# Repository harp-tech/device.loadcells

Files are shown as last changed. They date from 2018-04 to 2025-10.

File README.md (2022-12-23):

## Harp Load Cells Interface and Reader

This pair of boards can be used to acquire analog signals from load cells and output their data to a USB host. It is additionally able to emit programmable digital events.

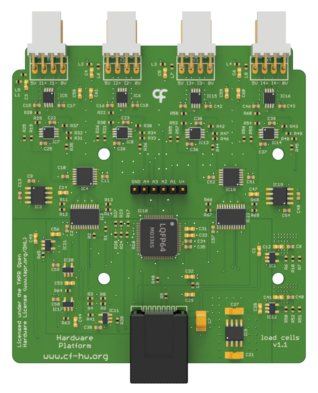
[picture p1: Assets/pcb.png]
harploadcellsinterface


### Key Features ###

* Load cells interface
  * Controls up to 2 load cells readers
  * Digital outputs can be regulated at 3V or 5V
* Load Cells Reader
  * Up to 4 load cell sensors
  * 1kHz sampling rate
  * Load cells offset compensation

### Connectivity ###

* Load cells interface
  * 1x BNC input signal (IN0)
  * 1x BNC output signal (Out0)
  * 1x screw terminal connector interface (GND, DOUT1 to DOUT8, DIN0)
  * 2x RJ45 for digital inputs (from load cells devices)
  * 1x stereo jack for clock sync input (CLKIN)
  * 1x USB (for computer)
  * 1x power barrel connector jack (12V only)
  * 1x screw terminal connector for 5V output (GND, +5V)
* Load Cells Reader
  * 4x flick lock connectors (X1 to X4) with 4 analog inputs each (5V, I+, I-, 0V)
  * 1x digital output [RJ45]

## Interface ##

The interface with the Harp board can be done through [Bonsai](https://bonsai-rx.org/) or a dedicated GUI (Graphical User Interface).

In order to use this GUI, there are some software that needs to be installed:

1 - Install the [drivers](https://bitbucket.org/fchampalimaud/downloads/downloads/UsbDriver-2.12.26.zip).

2 - Install the [runtime](https://bitbucket.org/fchampalimaud/downloads/downloads/Runtime-1.0.zip).

3 - Reboot the computer.

4 - Install the [GUI](https://bitbucket.org/fchampalimaud/downloads/downloads/Harp%20Load%20Cells%20v1.1.0.zip).

## Licensing ##

Each subdirectory will contain a license or, possibly, a set of licenses if it involves both hardware and software.

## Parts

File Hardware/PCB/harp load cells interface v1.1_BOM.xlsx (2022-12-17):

Part(s) | Quantity | Description | Distributor | Part. No.
IC1 | 1 | ESD Protection Low Cap | Mouser | 511-USBLC6-2SC6Y
IC2 | 1 | Conversores CC/CC sem isolação 12Vin, 0.591-6Vout 1.5A, Positive Logic | Mouser | 580-OKR-T/1.5-W12-C
IC3 | 1 | IC USB USB to Serial UART Enhanced IC SSOP-28 | Mouser | 895-FT232RL
IC4 | 1 | Reguladores de tensão de LDO High PSRR Fast RF High-Enable 1.5A | Mouser | 595-TPS78601DCQR
IC5 | 1 | Isoladores digitais Quad Ch 3.75V Iso 150M 2/2 NB, DO=LO | Mouser | 634-SI8642BC-B-IS1
IC6 | 1 | Microcontroladores de 8 bits - MCU 44TQFP, IND TEMP GREEN, 1.6-3.6V | Mouser | 556-ATXMEGA128A4U-AU
IC7 | 1 | LDO 250mA Ultra-Lo Noise LDO Reg | Mouser | 595-LP5907MFX-3.3NPB
IC8, IC9, IC10, IC11, IC12, IC13, IC14, IC15, IC16, IC17 | 10 | M74VHC1GT50DTT1G Buffer, Non-Inverting, 1.65V to 5.5V, SOT-23-5 | Mouser | 863-M74VHC1GT50DTT1G
C16 | 1 | CAP CER 13pF 50V ±5% C0G 0402 | Mouser | 81-GRM1555C1H130JA1D
C4, C5 | 2 | CAP CER 47pF 50V ±5% C0G 0402 | Mouser | 77-VJ0402A470JXACBC
CUSB | 1 | CAP CER 4.7nF 100V ±10% X7R 0402 | Mouser | 81-GRM155R72A472KA01
C2, C8, C10, C11, C15, C17, C19, C22, C23, C24, C25, C28, C29, C30, C31, C32, C33, C34, C35, C36, C37 | 21 | CAP CER 100nF 10V X5R 0402 | REEL | REEL
C26 | 1 | CAP CER 0.33uF 10V ±10% X5R 0402 | Mouser | GRM155R61A334KE15D
C9 | 1 | CAP TAN 4.7uF 6.3V ±10% 1206 | Mouser | 80-T491A475K006
C14, C18, C20, C21, C27 | 5 | CAP CER 10uF 10V ±10% X5R 0603 | Mouser | 81-GRM188R61A106KE9D
C1 | 1 | CAP TAN 22uF 20V ±10% 1210 | Mouser | 667-20TQC22MYFB
C3, C7 | 2 | CAP CER 22uF 25V ±10% X5R 1210 | Mouser | 81-GRM32ER61E226KE15
C12, C13 | 2 | CAP CER 47uF 10V ±10% X5R 1210 | Mouser | 81-GRM32ER61A476KE20
C6 | 1 | CAP ELE 100uF 25V ±20% | Mouser | 667-EEE-FK1E101P
R1 | 1 | RES SMD 0Ω OHM 5% 0402 | Mouser | 667-ERJ-2GE0R00X
R16, R17, R18, R19, R20, R21, R24, R25, R26, R27, R28, R29, R30, R31 | 14 | RES SMD 0402 33Ω, ± 1% | Mouser | 71-CRCW0402-33-E3
R15 | 1 | RES SMD 68Ω OHM 5% 0402 | Mouser | 71-CRCW0402-68-E3
RTRIM | 1 | RES SMD 243Ω OHM 1% 0402 | Mouser | 667-ERJ-2RKF2430X
R22 | 1 | RES SMD 330Ω OHM 1% 0402 | Mouser | 667-ERJ-PA2F3300X
R6 | 1 | RES SMD 30.9kΩ 1% 0402 | Mouser | 71-CRCW0402-30.9K-E3
R5 | 1 | RES SMD 95.3kΩ 1% 0402 | Mouser | 667-ERJ-2RKF9532X
R8, R10, R12, R14, R23 | 5 | RES SMD 100kΩ 1% 0402 | REEL | REEL
RUSB | 1 | RES SMD 1MΩ 1% 0402 | Mouser | 652-CR0402FX-1004GLF
F1 | 0 | 0603SFS100F/32-2 - Fuse, Surface Mount, 0603SFS Series, 1 A, 32 VDC, Slow Blow, 0603 | Mouser | 650-0603SFS100F/32-2
STATE | 1 | LED, Green, 1.6mm x 0.8mm, 566 nm, 2.1 V, 20 mA, 15 mcd | Mouser | 78-TLMP1100-GS08
OSC1 | 1 | 32MHz 10ppm | Mouser | 998-1001CI5032.0000T
CLKIN | 1 | SMT 3.5 STEREO REEL | Mouser | 502-35RASMT2BHNTRX
L2 | 1 | Indutores fixos LPS4012 Low Profile 1.5uH 2.2A 20% SMD | Mouser | 994-LPS4012-152MRB
L1 | 1 | 40ohms 100MHz 1.5A Monolithic 0805 SMD | Mouser | 875-MI0805K400R-10
PDI | 1 | 6P DR UNSHRD HRD | Mouser | 649-67996-206HLF
J1, J2 | 2 | Conectores modulares/Conectores de Ethernet 8/8 R/A MOD JACK | Mouser | 571-2158771
 | 2 | Ethernet Cable, Patch Lead, Cat5e, RJ45 Plug to RJ45 Plug, Beige, 500 mm | Farnell | 1526101
USB | 1 | UX60-MB-5S8 | Mouser | 798-UX60-MB-5S8
USB Cable | 1 | USB A - MINI-B 1M BLACK | Mouser | 538-88732-8602
 | 1 | Tubos de Luz LED CML LIGHTPIPE | Mouser | 606-7513D2-L
JACK | 1 | CC PCB 2.1MM | Mouser | 163-179PH-EX
WALL ADAPTER | 1 | AC/DC Power Supply, Class II, Fixed, 1 Output, 90 V, 264 V, 12 W, 12 V | Farnell | VEL12US120-EU-JA
J1 | 1 | C-Grid III 90120 Series, Through Hole, Header, 3 Contacts, 2.54 mm | Mouser | 538-90120-0763
Jumper | 1 | Jumper (Busbar), Shunt, PCB Connectors, 2, 2.54 mm | Farnell | 4218176
IN0, OUT0 | 2 | CONN BNC JACK R/A 50 OHM | Mouser | 571-5227161-1
 | 1 | 20.1550M/2-E - Pluggable Terminal Block, 3.5 mm, 2 Ways, 28 AWG, 16 AWG, 1.5 mm², Screw | Farnell | 2575215
 | 1 | 20.1550M/10-E - Pluggable Terminal Block, 3.5 mm, 10 Ways, 28 AWG, 16 AWG, 1.5 mm², Screw | Farnell | 2575213
X2 | 1 | 20.155MH/2-E - Terminal Block, Header, 3.5 mm, 2 Ways, 10 A, 250 V, Through Hole Right Angle | Farnell | 2517858
X1 | 1 | 20.155MH/10-E - Terminal Block, Header, 3.5 mm, 10 Ways, 10 A, 250 V, Through Hole Right Angle | Farnell | 2575221
 | 8 | 1110030 - Nut, Hex, M3, Nylon 6.6, Pack of 50 | Farnell | 1110030
 | 4 | Machine Screw, M3, 10 mm, Nylon (Polyamide), Pan Head Slotted, PK25 | Farnell | 1514410
Components | 116
Licensed under the TAPR Open Hardware License (www.tapr.org/OHL)
Copyright 2018 Artur Silva and Filipe Carvalho

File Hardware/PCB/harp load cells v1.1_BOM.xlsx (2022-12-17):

Part(s) | Quantity | Description | Distributor | Part. No.
IC1 | 1 | Reguladores de tensão de LDO 20V 200mA LDO adjVo | Mouser | 584-ADP7118AUJZ-R7
IC2, IC22 | 2 | CIs de potenciômetros digitais IC 4-CH | Mouser | 584-AD5204BRUZ10-R7
IC3, IC19 | 2 | Referências de tensão Ultra-High-Precision Ultra-Low-Noise 3V | Mouser | 700-MAX6126AASA30
IC4, IC18 | 2 | Amplificadores de precisão 55V Low Noise Zero Drift OpAmp 4x | Mouser | 584-ADA4522-4ARUZ
IC4, IC18 | 0 | Amplificadores operacionais - 2.2nV/rtHz,18MHz Prec,RRO,36V | Mouser | 595-OPA4209AIPW
IC10 | 1 | ADC 4Ch w/Bipolar 16B Simult Sampling | Mouser | 584-AD7606BSTZ-4
IC9 | 1 | Reguladores de tensão de comutação 125mA Swtc Cap Volt Converter | Mouser | 700-MAX1680ESA
IC7, IC8, IC13, IC14 | 4 | Amplificadores operacionais - Amp Op 36V,microPwr,RRO Dual | Mouser | 595-OPA2170AIDGKR
IC11 | 1 | SINGLE BUS BUFFER GATE | Mouser | 595-SN74LVC1G125DBVR
IC12 | 1 | Reguladores de tensão de LDO -30V 200mA lo-noise Linear Reg adj | Mouser | 584-ADP7182AUJZ-R7
IC5, IC6, IC15, IC16 | 4 | Amplificadores de instrumentação 3nV/Hz Low Power | Mouser | 584-AD8421ARMZ-R7
IC5, IC6, IC15, IC16 | 0 | Amplificadores de instrumentação 330 uA Rail to Rail | Mouser | 584-AD8422-ARMZ
IC21 | 1 | LDO 200mA Low IQ LDO Reg for Portables | Mouser | 595-TLV70030DDCR
IC17 | 1 | Inversores 3-5.5V Single TTL Schmitt Input | Mouser | 863-M74VHC1GT14DTT1G
IC20 | 1 | Buffers e line drivers Single Schmitt-Trgr | Mouser | 595-SN74LVC1G17DBVG4
C2, C9, C10, C11, C13, C15, C16, C17, C18, C19, C20, C22, C23, C24, C25, C26, C30, C36, C37, C38, C39, C40, C42, C43, C45, C46, C48, C50, C51, C52, C54, C55, C57 | 33 | SMD 0402 100nF 16V X7R ±5% | REEL | REEL
C8, C34, C35 | 3 | SMD 0402 1uF 10V X7S ±10% | Mouser | 81-GCM155C71A105ME8D
C14, C47, C53 | 3 | SMD 0603 1uF 6.3V X6S ±10% | Mouser | 81-GRM185C80J105KE26
C1, C12, C28, C41, C58, C59, C60, C61 | 8 | SMD 0402 2.2uF 25V X5R ±20% | Mouser | 81-GRM188R61E225ME4D
C49, C56 | 2 | SMD 0603 4.7uF 10V X5R ±20% | Mouser | 81-GRM185R61A475ME1D
C3, C4, C5, C6, C29, C31, C32, C33, C44 | 9 | SMD 0603 10uF 16V ±20% | Mouser | 81-GRM188R61C106MALD
C21, C27 | 2 | SMD 10uF 25V ±10% B Case Molded | Mouser | 74-293D106X9025B2TE3
C7 | 1 | CAP TAN 22uF 20V ±10% 1210 | Mouser | 667-20TQC22MYFB
R5 | 1 | SMD 0402 0Ohms ±5% | Mouser | 667-ERJ-2GE0R00X
R2, R39, R40, R41 | 4 | SMD 0402 33Ohms ±5% | Mouser | 667-ERJ-2GEJ330X
R15, R16, R61, R62 | 4 | SMD 0402 100Ohms ±0.1% | Mouser | 667-ERA-2AEB101X
R15, R16, R61, R62 | 0 | SMD 0402 200Ohms ±0.1% | Mouser | 667-ERA-2ARB201X
R19, R20, R21, R22, R25, R26, R29, R30, R31, R32, R33, R34, R46, R47, R48, R49, R53, R54, R55, R56, R57, R58, R59, R60 | 24 | SMD 0402 1kOhms ±0.1% | Mouser | 667-ERA-2AEB102X
R1, R3, R8 | 3 | SMD 0402 3kOhms ±5% | Mouser | 667-ERJ-2GEJ302X
R11, R12, R13, R14, R66, R67, R68, R69 | 8 | SMD 0402 5.1kOhms ±5% | Mouser | 667-ERJ-2RKF5101X
R7, R10, R51, R52 | 4 | SMD 0402 10kOhm | REEL | REEL
R63 | 1 | SMD 0402 20kOhms ±5% | Mouser | 667-ERJ-2GEJ203X
R50 | 1 | SMD 0402 29.4kOhms ±1% | Mouser | 667-ERJ-2RKF2942X
R6 | 1 | SMD 0402 30kOhms ±1% | Mouser | 667-ERJ-2RKF3002X
R64 | 1 | SMD 0402 40.2kOhms ±1% | Mouser | 667-ERJ-2RKF4022X
R18, R23, R27, R65 | 4 | SMD 0402 100kOhm | REEL | REEL
R35, R36, R37, R38, R42, R43, R44, R45 | 8 | SMD 0402 12kOhms ±1% | Mouser | 667-ERJ-U02F1202X | 100g
R35, R36, R37, R38, R42, R43, R44, R45 | 0 | SMD 0402 36kOhms ±1% | Mouser | 652-CR0402FX-3602GLF | 33.3g
L1, L2, L3, L4, L5, L6, L7, L8, L9 | 9 | Indutores fixos 1uH 20% | Mouser | 810-MLZ1005M1R0WT000
J1 | 1 | Conectores modulares/Conectores de Ethernet 8/8 R/A MOD JACK | Mouser | 571-2158771
JP1 | 1 | HEADER 6x1 2.54mm GOLD | Mouser | 68001-206HLF
X1, X2, X3, X4 | 4 | Distribuidores e Alojamento de Fios 4C RA F/L HEADER | Mouser | 538-22-05-7048
 | 4 | Receptacle, 4 Ways, 2.54 mm, 2759, 4809 Series Crimp Terminals | Mouser | 538-22-01-2045
 | 16 | CRIMP TERM 22-30 TIN | Mouser | 538-08-50-0114
 | 8 | 1110030 - Nut, Hex, M3, Nylon 6.6, Pack of 50 | Farnell | 1110030
 | 4 | Machine Screw, M3, 10 mm, Nylon (Polyamide), Pan Head Slotted, PK25 | Farnell | 1514410
Components | 194
Licensed under the TAPR Open Hardware License (www.tapr.org/OHL)
Copyright 2018 Artur Silva and Filipe Carvalho

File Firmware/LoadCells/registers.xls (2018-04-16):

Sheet: registers
Has event. | When | Type | Array | Array Len. | Register Name | Desciption | Mask Type | Value | Name | Desciption
no |  | U8 | no |  | START | Writing any value above ZERO will start the acquisition. ZERO will stop it. | bit | (1<<0) | START
yes | When a new sample is acquired | I16 | yes | 8 | LOAD_CELLS | Analog value of the Load Cells
yes | When DI0_CONF == DI0_SYNC and the input changes | U8 | no |  | DI0 | State of digital input 0 (DI0) | bit | (1<<0) | DI0
yes | When DO0_CONF == DO0_TGL_EACH_SEC | U8 | no |  | DO0 | State of digital output 0 (DO0) | bit | (1<<0) | DO0
no |  | U8 | no |  | THRESHOLDS | State of the filter thresholds -- This regiter is not used!!!
no |  | U8 | no |  | RESERVED0 | Reserved for future purposes
no |  | U8 | no |  | RESERVED1 | Reserved for future purposes
no |  | U8 | no |  | DI0_CONF | Configuration of the digital input 0 (DI0) | mask | (3<<0) | DI0_SEL
 |  |  |  |  |  |  | group_mask | (0<<0) | DI0_SYNC | Use as a pure digital input
 |  |  |  |  |  |  | group_mask | (1<<0) | DI0_RISE_START_ACQ | Start acquisition when rising edge and stop when falling edge
 |  |  |  |  |  |  | group_mask | (2<<0) | DI0_FALL_START_ACQ | Start acquisition when falling edge and stop when rising edge
no |  | U8 | no |  | DO0_CONF | Configuration of the digital output 0 (DO0) | mask | (3<<0) | DO0_SEL
 |  |  |  |  |  |  | group_mask | (0<<0) | DO0_DIG | Use as a pure digital output
 |  |  |  |  |  |  | group_mask | (1<<0) | DO0_TGL_EACH_SEC | Toogle each second when acquiring
 |  |  |  |  |  |  | group_mask | (2<<0) | DO0_PULSE | The digital output will be ONE during period specified by register DO0_PULSE
no |  | U8 | no |  | DO0_PULSE | Pulse for the digital output 0 (DO0) [1:255]
no |  | U16 | no |  | DO_SET | Set the digital outputs
no |  | U16 | no |  | DO_CLEAR | Clear the digital outputs
no |  | U16 | no |  | DO_TOGGLE | Toggle the digital outputs
yes | When the values where changed by a threshold filter | U16 | no |  | DO_OUT | Writes to the digital output
no |  | U8 | no |  | RESERVED2 | Reserved for future purposes
no |  | U8 | no |  | RESERVED3 | Reserved for future purposes
no |  | I16 | no |  | OFFSET_CH0 | Offset value of Load Cell channel 0 [-255:255]
no |  | I16 | no |  | OFFSET_CH1 | Offset value of Load Cell channel 1 [-255:255]
no |  | I16 | no |  | OFFSET_CH2 | Offset value of Load Cell channel 2 [-255:255]
no |  | I16 | no |  | OFFSET_CH3 | Offset value of Load Cell channel 3 [-255:255]
no |  | I16 | no |  | OFFSET_CH4 | Offset value of Load Cell channel 4 [-255:255]
no |  | I16 | no |  | OFFSET_CH5 | Offset value of Load Cell channel 5 [-255:255]
no |  | I16 | no |  | OFFSET_CH6 | Offset value of Load Cell channel 6 [-255:255]
no |  | I16 | no |  | OFFSET_CH7 | Offset value of Load Cell channel 7 [-255:255]
no |  | U8 | no |  | RESERVED4 | Reserved for future purposes
no |  | U8 | no |  | RESERVED5 | Reserved for future purposes
 |  | U8 | no |  | DO0_CH | Load Cell channel to be used to feed the threshold filter | mask | (16<<0) | DO_CH
 |  | U8 | no |  | DO1_CH |  | group_mask | (0<<0) | CH0 | Load Cell channel 0
 |  | U8 | no |  | DO2_CH |  | group_mask | (1<<0) | CH1 | Load Cell channel 1
 |  | U8 | no |  | DO3_CH |  | group_mask | (2<<0) | CH2 | Load Cell channel 2
 |  | U8 | no |  | DO4_CH |  | group_mask | (3<<0) | CH3 | Load Cell channel 3
 |  | U8 | no |  | DO5_CH |  | group_mask | (4<<0) | CH4 | Load Cell channel 4
 |  | U8 | no |  | DO6_CH |  | group_mask | (5<<0) | CH5 | Load Cell channel 5
 |  | U8 | no |  | DO7_CH |  | group_mask | (6<<0) | CH6 | Load Cell channel 6
 |  | I16 | no |  | DO0_TH_VALUE | Value to be compared | group_mask | (7<<0) | CH7 | Load Cell channel 7
 |  | I16 | no |  | DO1_TH_VALUE |  | group_mask | (8<<0) | SOFTWARE | Filter not used -- Use pin as a pure digital output
 |  | I16 | no |  | DO2_TH_VALUE
 |  | I16 | no |  | DO3_TH_VALUE
 |  | I16 | no |  | DO4_TH_VALUE
 |  | I16 | no |  | DO5_TH_VALUE
 |  | I16 | no |  | DO6_TH_VALUE
 |  | I16 | no |  | DO7_TH_VALUE
 |  | U16 | no |  | DO0_TH_UP_MS | Time (ms) above the configured threshold to set the digital output
 |  | U16 | no |  | DO1_TH_UP_MS
 |  | U16 | no |  | DO2_TH_UP_MS
 |  | U16 | no |  | DO3_TH_UP_MS
 |  | U16 | no |  | DO4_TH_UP_MS
 |  | U16 | no |  | DO5_TH_UP_MS
 |  | U16 | no |  | DO6_TH_UP_MS
 |  | U16 | no |  | DO7_TH_UP_MS
 |  | U16 | no |  | DO0_TH_DOWN_MS | Time (ms) below the configured threshold to set the digital output
 |  | U16 | no |  | DO1_TH_DOWN_MS
 |  | U16 | no |  | DO2_TH_DOWN_MS
 |  | U16 | no |  | DO3_TH_DOWN_MS
 |  | U16 | no |  | DO4_TH_DOWN_MS
 |  | U16 | no |  | DO5_TH_DOWN_MS
 |  | U16 | no |  | DO6_TH_DOWN_MS
 |  | U16 | no |  | DO7_TH_DOWN_MS
no |  | U8 | no |  | EVNT_ENABLE | Enable the Events | bit | (1<<0) | EVT_LOAD_CELLS | Event of register LOAD_CELLS
 |  |  |  |  |  |  | bit | (1<<1) | EVT_DI0 | Event of register DI0
 |  |  |  |  |  |  | bit | (1<<2) | EVT_DO0 | Event of register DO0
 |  |  |  |  |  |  | bit | (1<<3) | EVT_DO_OUT | Event of THRESHOLDS

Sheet: meta data
who am I: | 1232
firmware major version: | 1
firmware minor version: | 0
hardware major version: | 1
hardware minor version: | 0
assembly version: | 0
device name: | LoadCells

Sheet: ios
Pin Name | PORT | Pin | Direction | Use Input | Out | Out default | Pull | Sense | Int. priority | Int. number | Desciption | Neg. Output
DI0 | PORTB | 0 | input |  |  |  | up | both_edges | low | 0 | Input DIO
DO0 | PORTB | 1 | output | yes | digital | 0 |  |  |  |  | Output DO0 | no
DO1 | PORTA | 0 | output | yes | digital | 0 |  |  |  |  | Output DO1 | no
DO2 | PORTA | 1 | output | yes | digital | 0 |  |  |  |  | Output DO2 | no
DO3 | PORTA | 2 | output | yes | digital | 0 |  |  |  |  | Output DO3 | no
DO4 | PORTA | 3 | output | yes | digital | 0 |  |  |  |  | Output DO4 | no
DO5 | PORTA | 4 | output | yes | digital | 0 |  |  |  |  | Output DO5 | no
DO6 | PORTA | 5 | output | yes | digital | 0 |  |  |  |  | Output DO6 | no
DO7 | PORTA | 6 | output | yes | digital | 0 |  |  |  |  | Output DO7 | no
DO8 | PORTA | 7 | output | yes | digital | 0 |  |  |  |  | Output DO8 | no
CS0_2 | PORTC | 1 | output | yes | wire_and | 1 |  |  |  |  | CS0_2 / CS_POT0 | no
CS0_1 | PORTC | 0 | output | yes | wire_and | 1 |  |  |  |  | CS0_1 / CS_ADC0 | no
CS0_0 | PORTC | 4 | output | yes | digital | 1 |  |  |  |  | CS0_0 / CONVST0 | no
MOSI0 | PORTC | 5 | output | no | digital | 0 |  |  |  |  | MOSI0 | no
MISO0 | PORTC | 6 | input |  |  |  | up | both_edges | off | 0 | MISO0
SCK0 | PORTC | 7 | output | no | digital | 0 |  |  |  |  | SCK0 | no
CS1_2 | PORTD | 1 | output | yes | wire_and | 1 |  |  |  |  | CS1_2 / CS_POT1 | no
CS1_1 | PORTD | 0 | output | yes | wire_and | 1 |  |  |  |  | CS1_1 / CS_ADC1 | no
CS1_0 | PORTD | 4 | output | yes | digital | 1 |  |  |  |  | CS1_0 / CONVST1 | no
MOSI1 | PORTD | 5 | output | no | digital | 0 |  |  |  |  | MOSI1 | no
MISO1 | PORTD | 6 | input |  |  |  | up | both_edges | off | 0 | MISO1
SCK1 | PORTD | 7 | output | no | digital | 0 |  |  |  |  | SCK1 | no

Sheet: options
Array | Type | Array | Bits type | Direction | Use input | Pull | Sense | Int. priority | Int. number | Int. Mask | Out | Neg. Output
 |  |  |  | input | yes | up | both_edges | low | 0 |  | digital | yes
yes | U8 | yes | bit | output | no | down | rising_edge | med | 1 |  | wire_or | no
no | U16 | no | mask |  |  | tristate | falling_edge | high |  |  | wire_and
 | U32 |  | group_mask |  |  | busholder | low_level | off |  |  | wired_or_pull
 | U64 |  |  |  |  |  | no_interrupt |  |  |  | wired_and_pull
 | I8
 | I16
 | I32
 | I64
 | FLOAT

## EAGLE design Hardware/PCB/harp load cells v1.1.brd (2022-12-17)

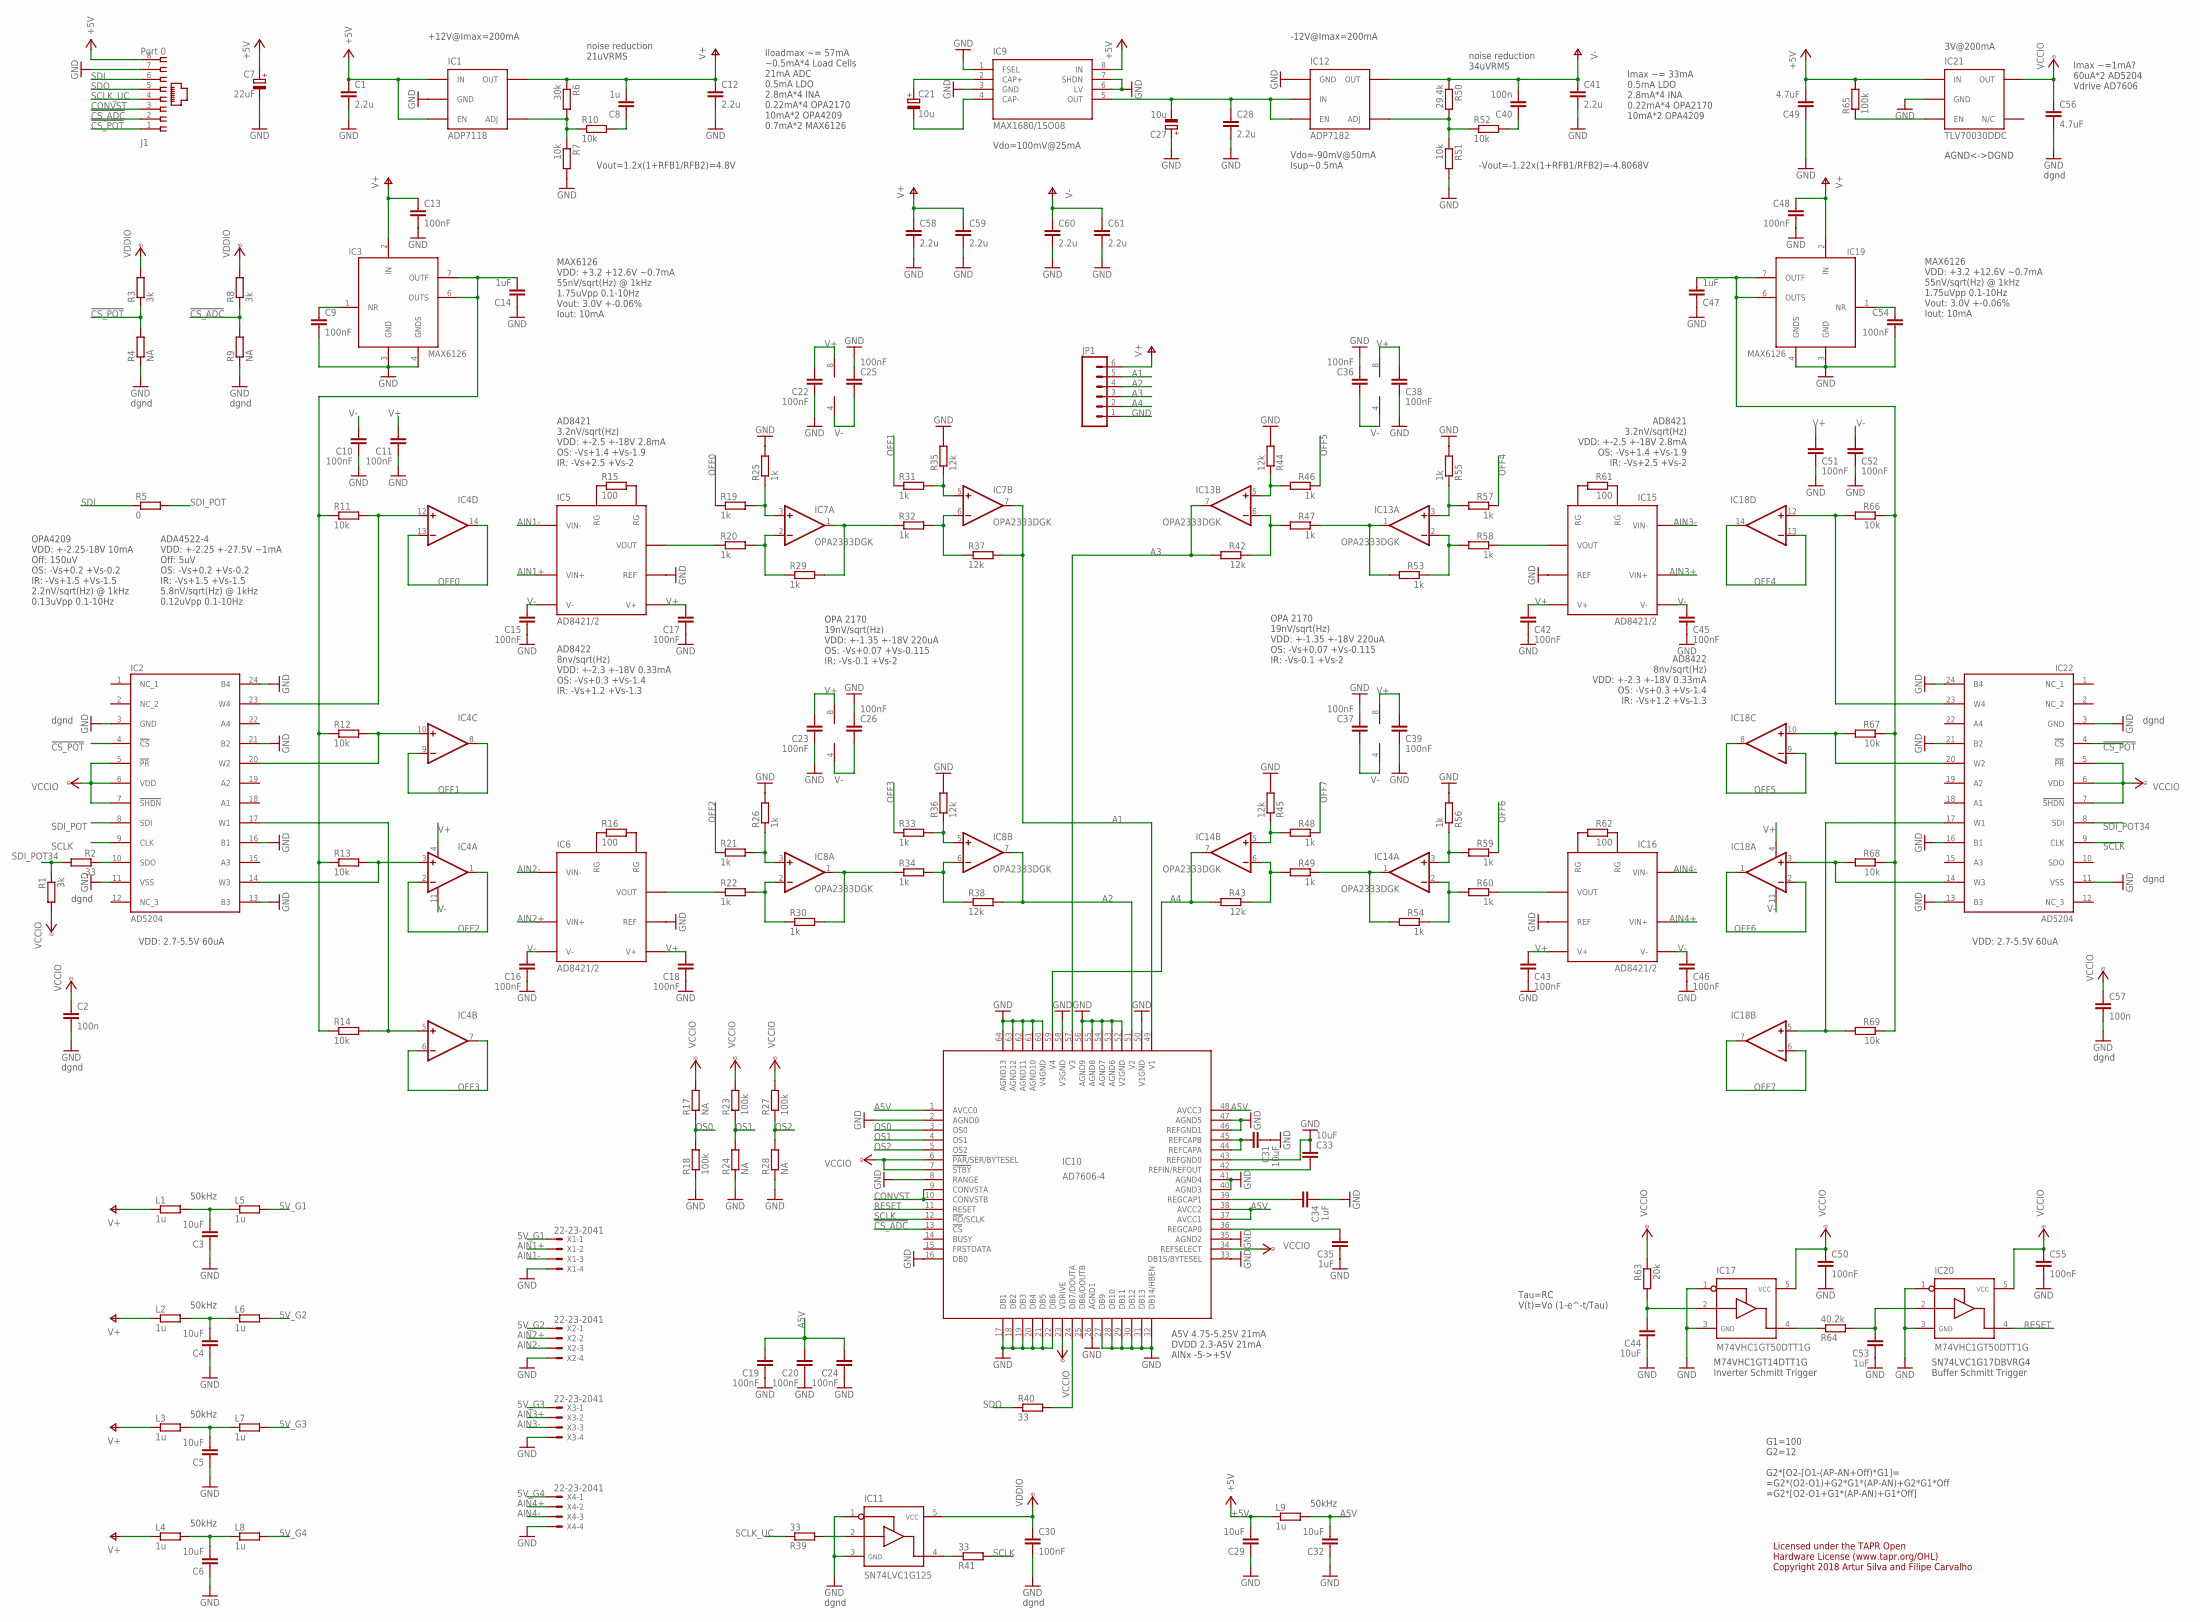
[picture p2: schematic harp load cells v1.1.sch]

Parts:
C1, C12, C28, C41, C58, C59, C60, C61: 2.2u; C0603
C2, C40, C57: 100n; C0402
C3, C4, C5, C6, C29, C31, C32, C33, C44: 10uF; C0603
C7: 22uF; CAP_100UF_HAND
C8: 1u; C0402
C9, C10, C11, C13, C15, C16, C17, C18, C19, C20, C22, C23, C24, C25, C26, C30, C36, C37, C38, C39, C42, C43, C45, C46, C48, C50, C51, C52, C54, C55: 100nF; C0402
C14, C47, C53: 1uF; C0603
C21, C27: 10u; A/3216-18W
C34, C35: 1uF; C0402
C49, C56: 4.7uF; C0603
IC1: ADP7118; TSOT23-5
IC2, IC22: AD5204; TSSOP-24
IC3, IC19: MAX6126; SO08
IC4, IC18: OPA4336T; TSSOP-14
IC5, IC6, IC15, IC16: AD8421/2; MSOP8
IC7, IC8, IC13, IC14: OPA2333DGK; MSOP08
IC9: MAX1680/1SO08; SO08
IC10: AD7606-4; LQFP-64
IC11: SN74LVC1G125; SOT23-5
IC12: ADP7182; TSOT23-5
IC17, IC20: M74VHC1GT50DTT1G; SOT23-5
IC21: TLV70030DDC; TSOT23-5
J1: Port 0; 520426-4
JP1: M06NO_SILK; 1X06_NO_SILK
L1, L2, L3, L4, L5, L6, L7, L8, L9: 1u; R0402
R1, R3, R8: 3k; R0402
R2, R39, R40, R41: 33; R0402
R4, R9, R17, R24, R28: NA; R0402
R5: 0; R0402
R6: 30k; R0402
R7, R10, R11, R12, R13, R14, R51, R52, R66, R67, R68, R69: 10k; R0402
R15, R16, R61, R62: 100; R0402
R18, R23, R27, R65: 100k; R0402
R19, R20, R21, R22, R25, R26, R29, R30, R31, R32, R33, R34, R46, R47, R48, R49, R53, R54, R55, R56, R57, R58, R59, R60: 1k; R0402
R35, R36, R37, R38, R42, R43, R44, R45: 12k; R0402
R50: 29.4k; R0402
R63: 20k; R0402
R64: 40.2k; R0402
X1, X2, X3, X4: 22-23-2041

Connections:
5V_G1: L5.2, X1.1
5V_G2: L6.2, X2.1
5V_G3: L7.2, X3.1
5V_G4: L8.2, X4.1
!CS_ADC: IC10.13 (!CS), J1.2, R8.1, R9.2
!CS_POT: IC2.4 (!CS), IC22.4 (!CS), J1.1, R3.1, R4.2
+5V: C1.1, C7.+, C29.2, C49.2, IC1.1 (IN), IC1.3 (EN), IC9.8 (IN), IC21.1 (IN), J1.8, L9.1, R65.2
A1: IC7.7 (OUT), IC10.49 (V1), JP1.5, R37.2
A2: IC8.7 (OUT), IC10.51 (V2), JP1.4, R38.2
A3: IC10.57 (V3), IC13.7 (OUT), JP1.3, R42.2
A4: IC10.59 (V4), IC14.7 (OUT), JP1.2, R43.2
A5V: C19.2, C20.2, C24.2, C32.2, IC10.1 (AVCC0), IC10.37 (AVCC1), IC10.38 (AVCC2), IC10.48 (AVCC3), L9.2
AIN1+: IC5.P$4 (VIN+), X1.2
AIN1-: IC5.P$1 (VIN-), X1.3
AIN2+: IC6.P$4 (VIN+), X2.2
AIN2-: IC6.P$1 (VIN-), X2.3
AIN3+: IC15.P$4 (VIN+), X3.2
AIN3-: IC15.P$1 (VIN-), X3.3
AIN4+: IC16.P$4 (VIN+), X4.2
AIN4-: IC16.P$1 (VIN-), X4.3
CONVST: IC10.9 (CONVSTA), IC10.10 (CONVSTB), J1.3
GND: C1.2, C2.2, C3.1, C4.1, C5.1, C6.1, C7.-, C9.2, C10.1, C11.1, C12.2, C13.2, C14.1, C15.1, C16.1, C17.1, C18.1, C19.1, C20.1, C22.1, C23.1, C24.1, C25.1, C26.1, C27.+, C28.2, C29.1, C30.2, C31.1, C32.1, C33.1, C34.1, C35.1, C36.1, C37.1, C38.1, C39.1, C41.2, C42.1, C43.1, C44.1, C45.1, C46.1, C47.1, C48.2, C49.1, C50.2, C51.1, C52.1, C53.1, C54.2, C55.2, C56.2, C57.2, C58.2, C59.2, C60.2, C61.2, IC1.2 (GND), IC2.3 (GND), IC2.11 (VSS), IC2.13 (B3), IC2.16 (B1), IC2.21 (B2), IC2.24 (B4), IC3.3 (GND), IC3.4 (GNDS), IC5.P$6 (REF), IC6.P$6 (REF), IC9.1 (FSEL), IC9.3 (GND), IC9.6 (LV), IC9.7 (SHDN), IC10.2 (AGND0), IC10.8 (RANGE), IC10.16 (DB0), IC10.17 (DB1), IC10.18 (DB2), IC10.19 (DB3), IC10.20 (DB4), IC10.21 (DB5), IC10.22 (DB6), IC10.26 (AGND1), IC10.27 (DB9), IC10.28 (DB10), IC10.29 (DB11), IC10.30 (DB12), IC10.31 (DB13), IC10.32 (DB14/HBEN), IC10.33 (DB15/BYTESEL), IC10.35 (AGND2), IC10.40 (AGND3), IC10.41 (AGND4), IC10.43 (REFGND0), IC10.46 (REFGND1), IC10.47 (AGND5), IC10.50 (V1GND), IC10.52 (V2GND), IC10.53 (AGND6), IC10.54 (AGND7), IC10.55 (AGND8), IC10.56 (AGND9), IC10.58 (V3GND), IC10.60 (V4GND), IC10.61 (AGND10), IC10.62 (AGND11), IC10.63 (AGND12), IC10.64 (AGND13), IC11.1, IC11.3, IC12.1 (GND), IC15.P$6 (REF), IC16.P$6 (REF), IC17.1, IC17.3, IC19.3 (GND), IC19.4 (GNDS), IC20.1, IC20.3, IC21.2 (GND), IC22.3 (GND), IC22.11 (VSS), IC22.13 (B3), IC22.16 (B1), IC22.21 (B2), IC22.24 (B4), J1.7, JP1.1, R4.1, R7.2, R9.1, R18.1, R24.1, R25.2, R26.2, R28.1, R35.2, R36.2, R44.2, R45.2, R51.2, R55.2, R56.2, X1.4, X2.4, X3.4, X4.4
unnamed: IC21.3 (EN), R65.1
unnamed: IC12.4 (ADJ), R50.2, R51.1, R52.1
unnamed: C44.2, IC17.2, R63.2
unnamed: C35.2, IC10.36 (REGCAP0)
unnamed: IC6.P$7 (VOUT), R22.1
unnamed: C40.1, R52.2
unnamed: C6.2, L4.2, L8.1
unnamed: IC17.4, R64.1
unnamed: C21.+, IC9.2 (CAP+)
unnamed: C21.-, IC9.4 (CAP-)
unnamed: C27.-, C28.1, IC9.5 (OUT), IC12.2 (IN), IC12.3 (EN)
unnamed: C53.2, IC20.2, R64.2
unnamed: IC7.6 (-IN), R32.2, R37.1
unnamed: C34.2, IC10.39 (REGCAP1)
unnamed: IC13.2 (-IN), R53.1, R58.2
unnamed: IC7.2 (-IN), R20.2, R29.1
unnamed: IC7.3 (+IN), R19.2, R25.1
unnamed: IC7.5 (+IN), R31.2, R35.1
unnamed: C33.2, IC10.42 (REFIN/REFOUT)
unnamed: IC13.3 (+IN), R55.1, R57.2
unnamed: IC13.6 (-IN), R42.1, R47.2
unnamed: IC13.5 (+IN), R44.1, R46.2
unnamed: C31.2, IC10.44 (REFCAPA), IC10.45 (REFCAPB)
unnamed: C8.1, R10.2
unnamed: IC1.4 (ADJ), R6.2, R7.1, R10.1
unnamed: IC5.P$2 (RG), R15.2
unnamed: IC5.P$3 (RG), R15.1
unnamed: IC5.P$7 (VOUT), R20.1
unnamed: IC8.2 (-IN), R22.2, R30.1
unnamed: IC6.P$2 (RG), R16.2
unnamed: IC6.P$3 (RG), R16.1
unnamed: IC8.3 (+IN), R21.2, R26.1
unnamed: IC7.1 (OUT), R29.2, R32.1
unnamed: IC8.6 (-IN), R34.2, R38.1
unnamed: C9.1, IC3.1 (NR)
unnamed: IC8.5 (+IN), R33.2, R36.1
unnamed: IC15.P$2 (RG), R61.2
unnamed: IC8.1 (OUT), R30.2, R34.1
unnamed: IC15.P$3 (RG), R61.1
unnamed: IC15.P$7 (VOUT), R58.1
unnamed: IC2.20 (W2), IC4.10 (+IN), R12.2
unnamed: IC16.P$2 (RG), R62.2
unnamed: IC2.17 (W1), IC4.5 (+IN), R14.2
unnamed: IC16.P$3 (RG), R62.1
unnamed: C14.2, IC3.6 (OUTS), IC3.7 (OUTF), R11.1, R12.1, R13.1, R14.1
unnamed: IC18.10 (+IN), IC22.20 (W2), R67.2
unnamed: IC18.12 (+IN), IC22.23 (W4), R66.2
unnamed: IC11.2, R39.2
unnamed: IC2.10 (SDO), R2.1
unnamed: C5.2, L3.2, L7.1
unnamed: IC18.3 (+IN), IC22.14 (W3), R68.2
unnamed: IC18.5 (+IN), IC22.17 (W1), R69.2
unnamed: IC13.1 (OUT), R47.1, R53.2
unnamed: C54.1, IC19.1 (NR)
unnamed: C47.2, IC19.6 (OUTS), IC19.7 (OUTF), R66.1, R67.1, R68.1, R69.1
unnamed: IC2.14 (W3), IC4.3 (+IN), R13.2
unnamed: IC14.2 (-IN), R54.1, R60.2
unnamed: IC14.3 (+IN), R56.1, R59.2
unnamed: IC14.6 (-IN), R43.1, R49.2
unnamed: IC14.5 (+IN), R45.1, R48.2
unnamed: IC2.23 (W4), IC4.12 (+IN), R11.2
unnamed: IC11.4, R41.1
unnamed: IC14.1 (OUT), R49.1, R54.2
unnamed: IC16.P$7 (VOUT), R60.1
unnamed: C4.2, L2.2, L6.1
unnamed: C3.2, L1.2, L5.1
unnamed: IC10.24 (DB7/DOUTA), R40.2
OFF0: IC4.13 (-IN), IC4.14 (OUT), R19.1
OFF1: IC4.8 (OUT), IC4.9 (-IN), R31.1
OFF2: IC4.1 (OUT), IC4.2 (-IN), R21.1
OFF3: IC4.6 (-IN), IC4.7 (OUT), R33.1
OFF4: IC18.13 (-IN), IC18.14 (OUT), R57.1
OFF5: IC18.8 (OUT), IC18.9 (-IN), R46.1
OFF6: IC18.1 (OUT), IC18.2 (-IN), R59.1
OFF7: IC18.6 (-IN), IC18.7 (OUT), R48.1
OS0: IC10.3 (OS0), R17.1, R18.2
OS1: IC10.4 (OS1), R23.1, R24.2
OS2: IC10.5 (OS2), R27.1, R28.2
RESET: IC10.11 (RESET), IC20.4
SCLK: IC2.9 (CLK), IC10.12 (!RD!/SCLK), IC22.9 (CLK), R41.2
SCLK_UC: J1.4, R39.1
SDI: J1.6, R5.1
SDI_POT: IC2.8 (SDI), R5.2
SDI_POT34: IC22.8 (SDI), R1.1, R2.2
SDO: J1.5, R40.1
V+: C8.2, C11.2, C12.1, C13.1, C17.2, C18.2, C22.2, C23.2, C38.2, C39.2, C42.2, C43.2, C48.1, C51.2, C58.1, C59.1, IC1.5 (OUT), IC3.2 (IN), IC4.4 (V+), IC5.P$8 (V+), IC6.P$8 (V+), IC7.8 (V+), IC8.8 (V+), IC13.8 (V+), IC14.8 (V+), IC15.P$8 (V+), IC16.P$8 (V+), IC18.4 (V+), IC19.2 (IN), JP1.6, L1.1, L2.1, L3.1, L4.1, R6.1
V-: C10.2, C15.2, C16.2, C25.2, C26.2, C36.2, C37.2, C40.2, C41.1, C45.2, C46.2, C52.2, C60.1, C61.1, IC4.11 (V-), IC5.P$5 (V-), IC6.P$5 (V-), IC7.4 (V-), IC8.4 (V-), IC12.5 (OUT), IC13.4 (V-), IC14.4 (V-), IC15.P$5 (V-), IC16.P$5 (V-), IC18.11 (V-), R50.1
VCCIO: C2.1, C30.1, C50.1, C55.1, C56.1, C57.1, IC2.5 (!PR), IC2.6 (VDD), IC2.7 (!SHDN), IC10.6 (!PAR!/SER/BYTESEL), IC10.7 (!STBY), IC10.23 (VDRIVE), IC10.34 (REFSELECT), IC11.5, IC17.5, IC20.5, IC21.5 (OUT), IC22.5 (!PR), IC22.6 (VDD), IC22.7 (!SHDN), R1.2, R3.2, R8.2, R17.2, R23.2, R27.2, R63.1

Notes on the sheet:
A5V 4.75-5.25V 21mA DVDD 2.3-A5V 21mA AINx -5->+5V
AD8421 3.2nV/sqrt(Hz) VDD: +-2.5 +-18V 2.8mA OS: -Vs+1.4 +Vs-1.9 IR: -Vs+2.5 +Vs-2
VDD: 2.7-5.5V 60uA
3V@200mA
50kHz
Licensed under the TAPR Open Hardware License (www.tapr.org/OHL) Copyright 2018 Artur Silva and Filipe Carvalho
Imax ~=1mA? 60uA*2 AD5204 Vdrive AD7606
AGND<->DGND
M74VHC1GT14DTT1G Inverter Schmitt Trigger
SN74LVC1G17DBVRG4 Buffer Schmitt Trigger
Tau=RC V(t)=Vo (1-e^-t/Tau)
dgnd
noise reduction 34uVRMS
-12V@Imax=200mA
-Vout=-1.22x(1+RFB1/RFB2)=-4.8068V
+12V@Imax=200mA
Vout=1.2x(1+RFB1/RFB2)=4.8V
noise reduction 21uVRMS
OPA4209 VDD: +-2.25-18V 10mA Off: 150uV OS: -Vs+0.2 +Vs-0.2 IR: -Vs+1.5 +Vs-1.5 2.2nV/sqrt(Hz) @ 1kHz 0.13uVpp 0.1-10Hz
Vdo=100mV@25mA
Vdo=-90mV@50mA Isup~0.5mA
AD8422 8nv/sqrt(Hz) VDD: +-2.3 +-18V 0.33mA OS: -Vs+0.3 +Vs-1.4 IR: -Vs+1.2 +Vs-1.3
Imax ~= 33mA 0.5mA LDO 2.8mA*4 INA 0.22mA*4 OPA2170 10mA*2 OPA4209
OPA 2170 19nV/sqrt(Hz) VDD: +-1.35 +-18V 220uA OS: -Vs+0.07 +Vs-0.115 IR: -Vs-0.1 +Vs-2
ADA4522-4 VDD: +-2.25 +-27.5V ~1mA Off: 5uV OS: -Vs+0.2 +Vs-0.2 IR: -Vs+1.5 +Vs-1.5 5.8nV/sqrt(Hz) @ 1kHz 0.12uVpp 0.1-10Hz
MAX6126 VDD: +3.2 +12.6V ~0.7mA 55nV/sqrt(Hz) @ 1kHz 1.75uVpp 0.1-10Hz Vout: 3.0V +-0.06% Iout: 10mA
Iloadmax ~= 57mA ~0.5mA*4 Load Cells 21mA ADC 0.5mA LDO 2.8mA*4 INA 0.22mA*4 OPA2170 10mA*2 OPA4209 0.7mA*2 MAX6126
G1=100 G2=12 G2*[O2-[O1-(AP-AN+Off)*G1]= =G2*(O2-O1)+G2*G1*(AP-AN)+G2*G1*Off =G2*[O2-O1+G1*(AP-AN)+G1*Off]

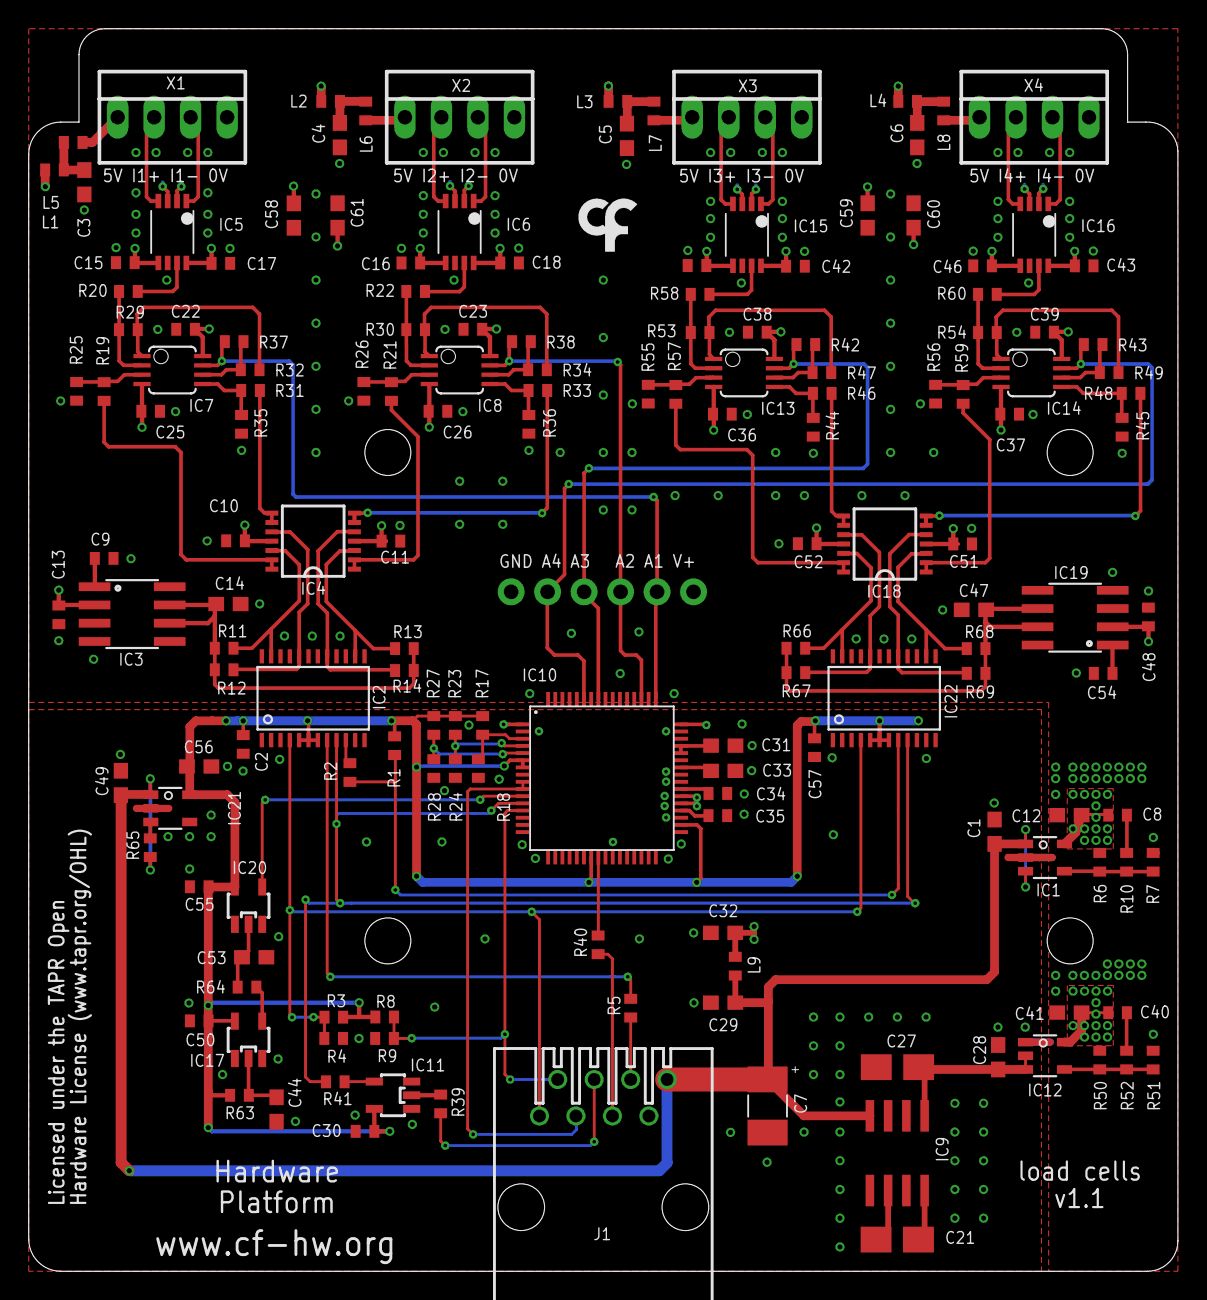
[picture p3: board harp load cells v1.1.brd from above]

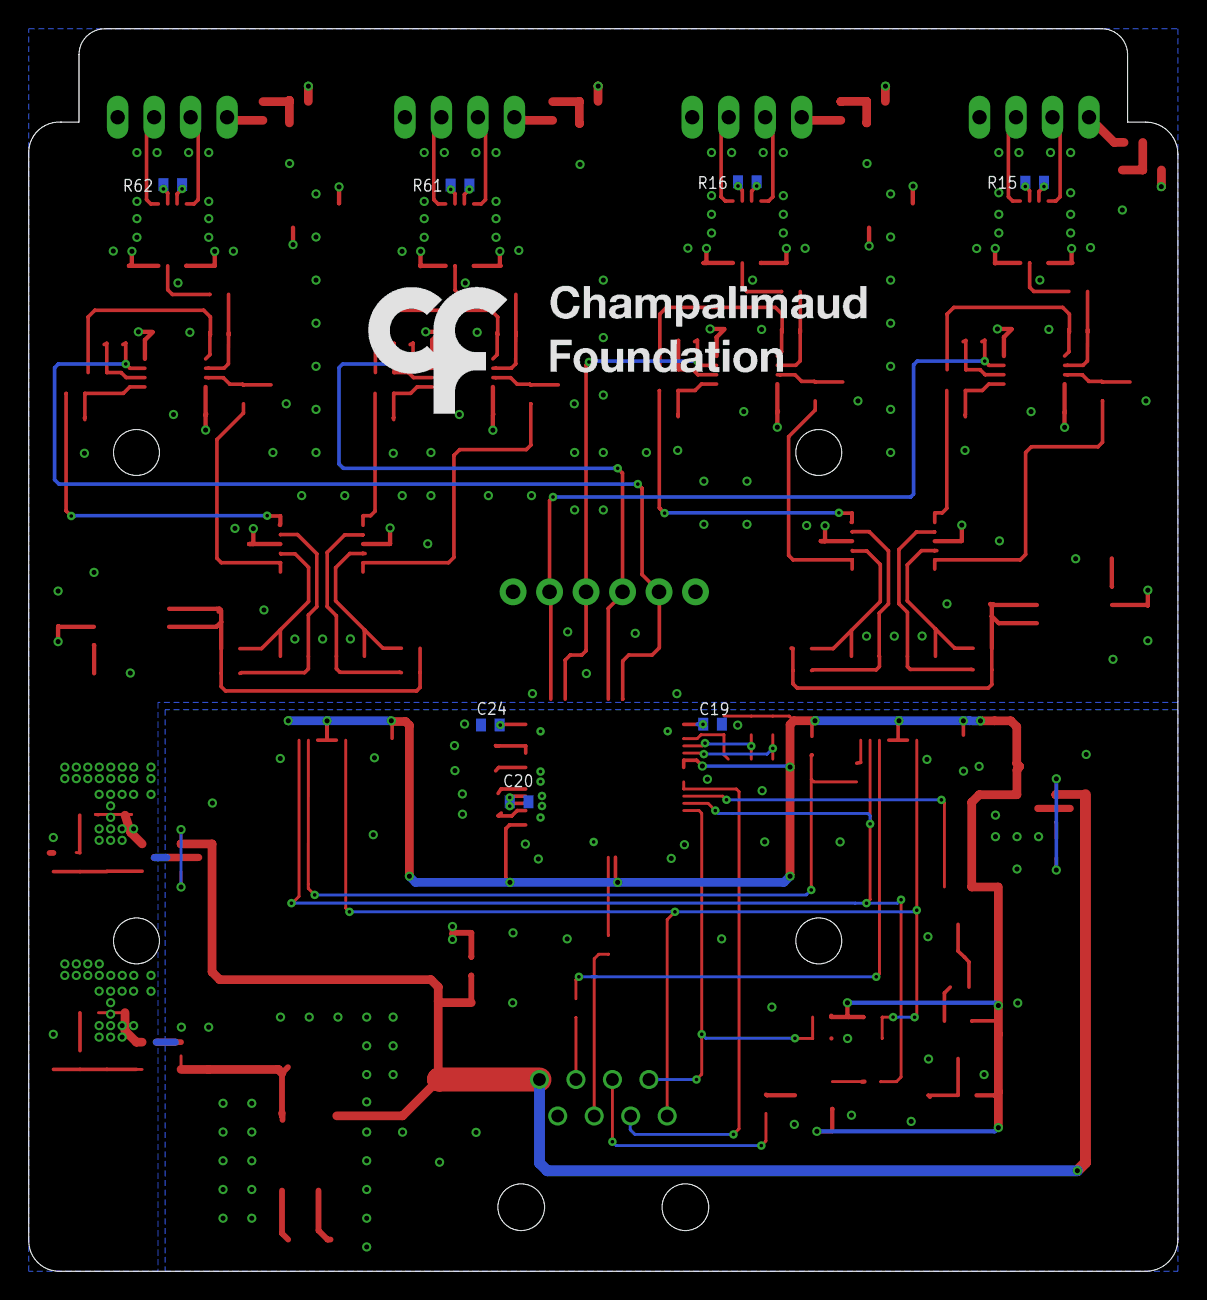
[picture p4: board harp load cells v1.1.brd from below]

Board: 4 copper layers, 80.0 x 86.5 mm, 169 parts (8 on the bottom side), 110 nets.

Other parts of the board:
U$1: LOGO_5
U$4: LOGO_7

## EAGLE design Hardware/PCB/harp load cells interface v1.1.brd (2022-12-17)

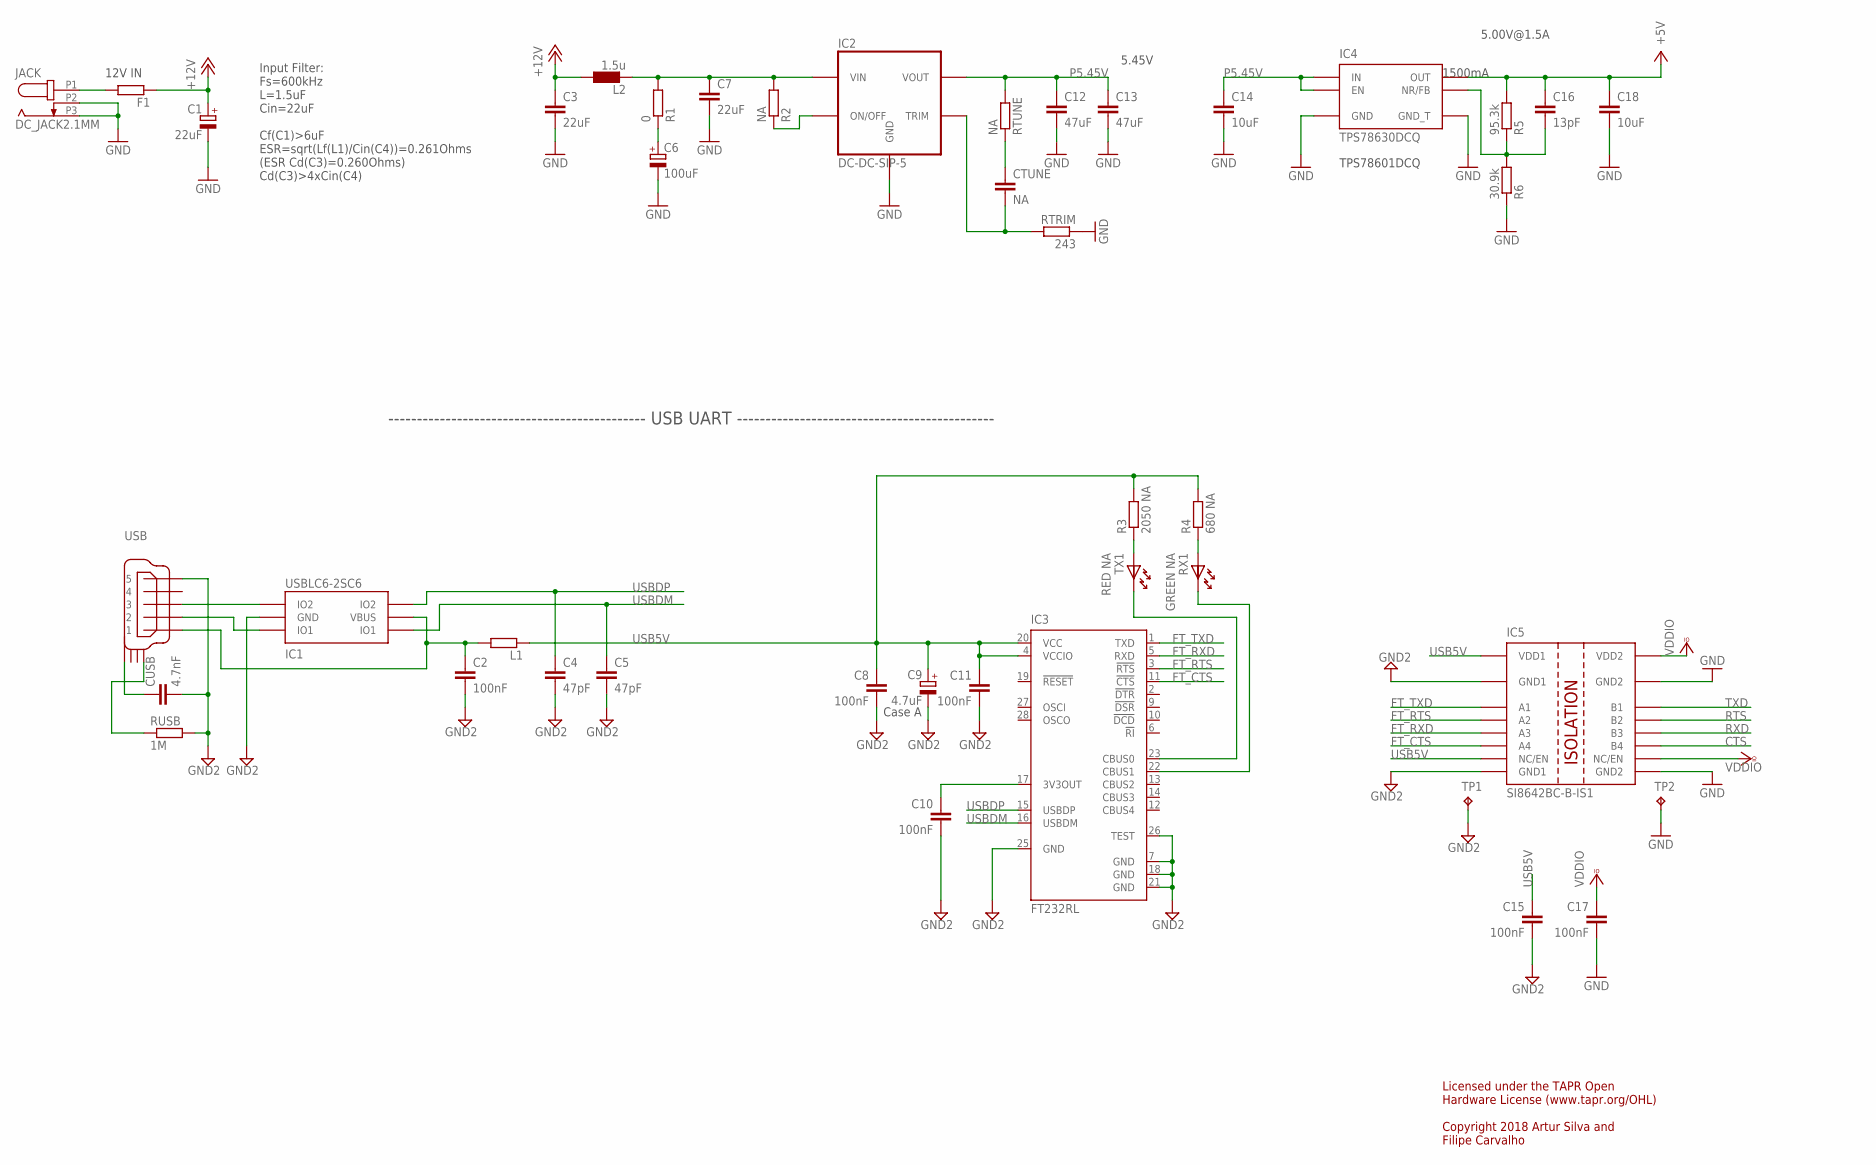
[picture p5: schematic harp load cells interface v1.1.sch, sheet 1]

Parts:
C1: 22uF; CAP_100UF_HAND
C2, C8, C10, C11, C15, C17: 100nF; C0402
C3, C7: 22uF; C1210
C4, C5: 47pF; C0402
C6: 100uF; PANASONIC_E
C9: 4.7uF; A/3216-18W
C12, C13: 47uF; C1210
C14, C18: 10uF; C0603
C16: 13pF; C0402
CTUNE: NA; C0402
CUSB: 4.7nF; C0402
F1: 1A FB; R0603
IC1: USBLC6-2SC6; SOT23-6L
IC2: DC-DC-SIP-5; SIP-5
IC3: FT232RL; SSOP28
IC4: TPS78630DCQ; SOT223-6
IC5: SI8642BC-B-IS1; NSOIC-16
JACK: DC_JACK2.1MM; DC_POWER_INPUT_2.1MM
L1: ???; R0805
L2: 1.5u; IND_LPS4012
R1: 0; R0402
R2: NA; R0402
R3: 2050 NA; R0402
R4: 680 NA; R0402
R5: 95.3k; R0402
R6: 30.9k; R0402
RTRIM: 243; R0402
RTUNE: NA; R0402
RUSB: 1M; R0402
RX1: GREEN NA; LED_HAND
TP1, TP2: TPTP08SQ; TP08SQ
TX1: RED NA; LED_HAND
USB: USB_MINI_B; 240-0002-1

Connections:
3V3OUT: C10.1, IC3.17 (3V3OUT)
+5V: C16.1, C18.1, IC4.P$4 (OUT), R5.2; also elsewhere on the board
+12V: C1.+, C3.1, F1.1, L2.1
CTS: IC5.11 (B4); also elsewhere on the board
DCIN: C7.1, IC2.P2 (VIN), L2.2, R1.2, R2.2
FT_CTS: IC3.11 (!CTS), IC5.6 (A4)
FT_RTS: IC3.3 (!RTS), IC5.4 (A2)
FT_RXD: IC3.5 (RXD), IC5.5 (A3)
FT_TXD: IC3.1 (TXD), IC5.3 (A1)
GND: C1.-, C3.2, C6.-, C7.2, C12.2, C13.2, C14.2, C17.2, C18.2, IC2.P3 (GND), IC4.P$3 (GND), IC4.P$6 (GND_T), IC5.9 (GND2), IC5.15 (GND2), JACK.P2 (2), JACK.P3 (3), R6.1, RTRIM.1, TP2.TP; also elsewhere on the board
GND2: C2.2, C4.2, C5.2, C8.2, C9.-, C10.2, C11.2, C15.2, CUSB.2, IC1.P$2 (GND), IC3.7 (GND), IC3.18 (GND), IC3.21 (GND), IC3.25 (GND), IC3.26 (TEST), IC5.2 (GND1), IC5.8 (GND1), RUSB.2, TP1.TP, USB.P$5 (5)
unnamed: R4.1, RX1.A
unnamed: IC3.22 (CBUS1), RX1.K
unnamed: CTUNE.2, IC2.P5 (TRIM), RTRIM.2
unnamed: IC1.P$3 (IO2), USB.P$3 (3)
unnamed: CTUNE.1, RTUNE.1
unnamed: CUSB.1, USB.SHIELD_4
unnamed: IC2.P1 (ON/OFF), R2.1
unnamed: F1.2, JACK.P1 (1)
unnamed: C16.2, IC4.P$5 (NR/FB), R5.1, R6.2
unnamed: C6.+, R1.1
unnamed: C2.1, IC1.P$5 (VBUS), L1.2, USB.P$1 (1)
unnamed: R3.1, TX1.A
unnamed: IC3.23 (CBUS0), TX1.K
unnamed: RUSB.1, USB.SHIELD_1
unnamed: IC1.P$1 (IO1), USB.P$2 (2)
P5.45V: C12.1, C13.1, C14.1, IC2.P4 (VOUT), IC4.P$1 (EN), IC4.P$2 (IN), RTUNE.2
RTS: IC5.13 (B2); also elsewhere on the board
RXD: IC5.12 (B3); also elsewhere on the board
TXD: IC5.14 (B1); also elsewhere on the board
USB5V: C8.1, C9.+, C11.1, C15.1, IC3.4 (VCCIO), IC3.20 (VCC), IC5.1 (VDD1), IC5.7 (NC/EN), L1.1, R3.2, R4.2
USBDM: C5.1, IC1.P$6 (IO1), IC3.16 (USBDM)
USBDP: C4.1, IC1.P$4 (IO2), IC3.15 (USBDP)
VCCIO: C17.1, IC5.10 (NC/EN), IC5.16 (VDD2); also elsewhere on the board

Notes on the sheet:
Licensed under the TAPR Open Hardware License (www.tapr.org/OHL) Copyright 2018 Artur Silva and Filipe Carvalho
12V IN
5.45V
1500mA
TPS78601DCQ
5.00V@1.5A
Input Filter: Fs=600kHz L=1.5uF Cin=22uF Cf(C1)>6uF ESR=sqrt(Lf(L1)/Cin(C4))=0.261Ohms (ESR Cd(C3)=0.260Ohms) Cd(C3)>4xCin(C4)
Case A
--------------------------------------------- USB UART ---------------------------------------------

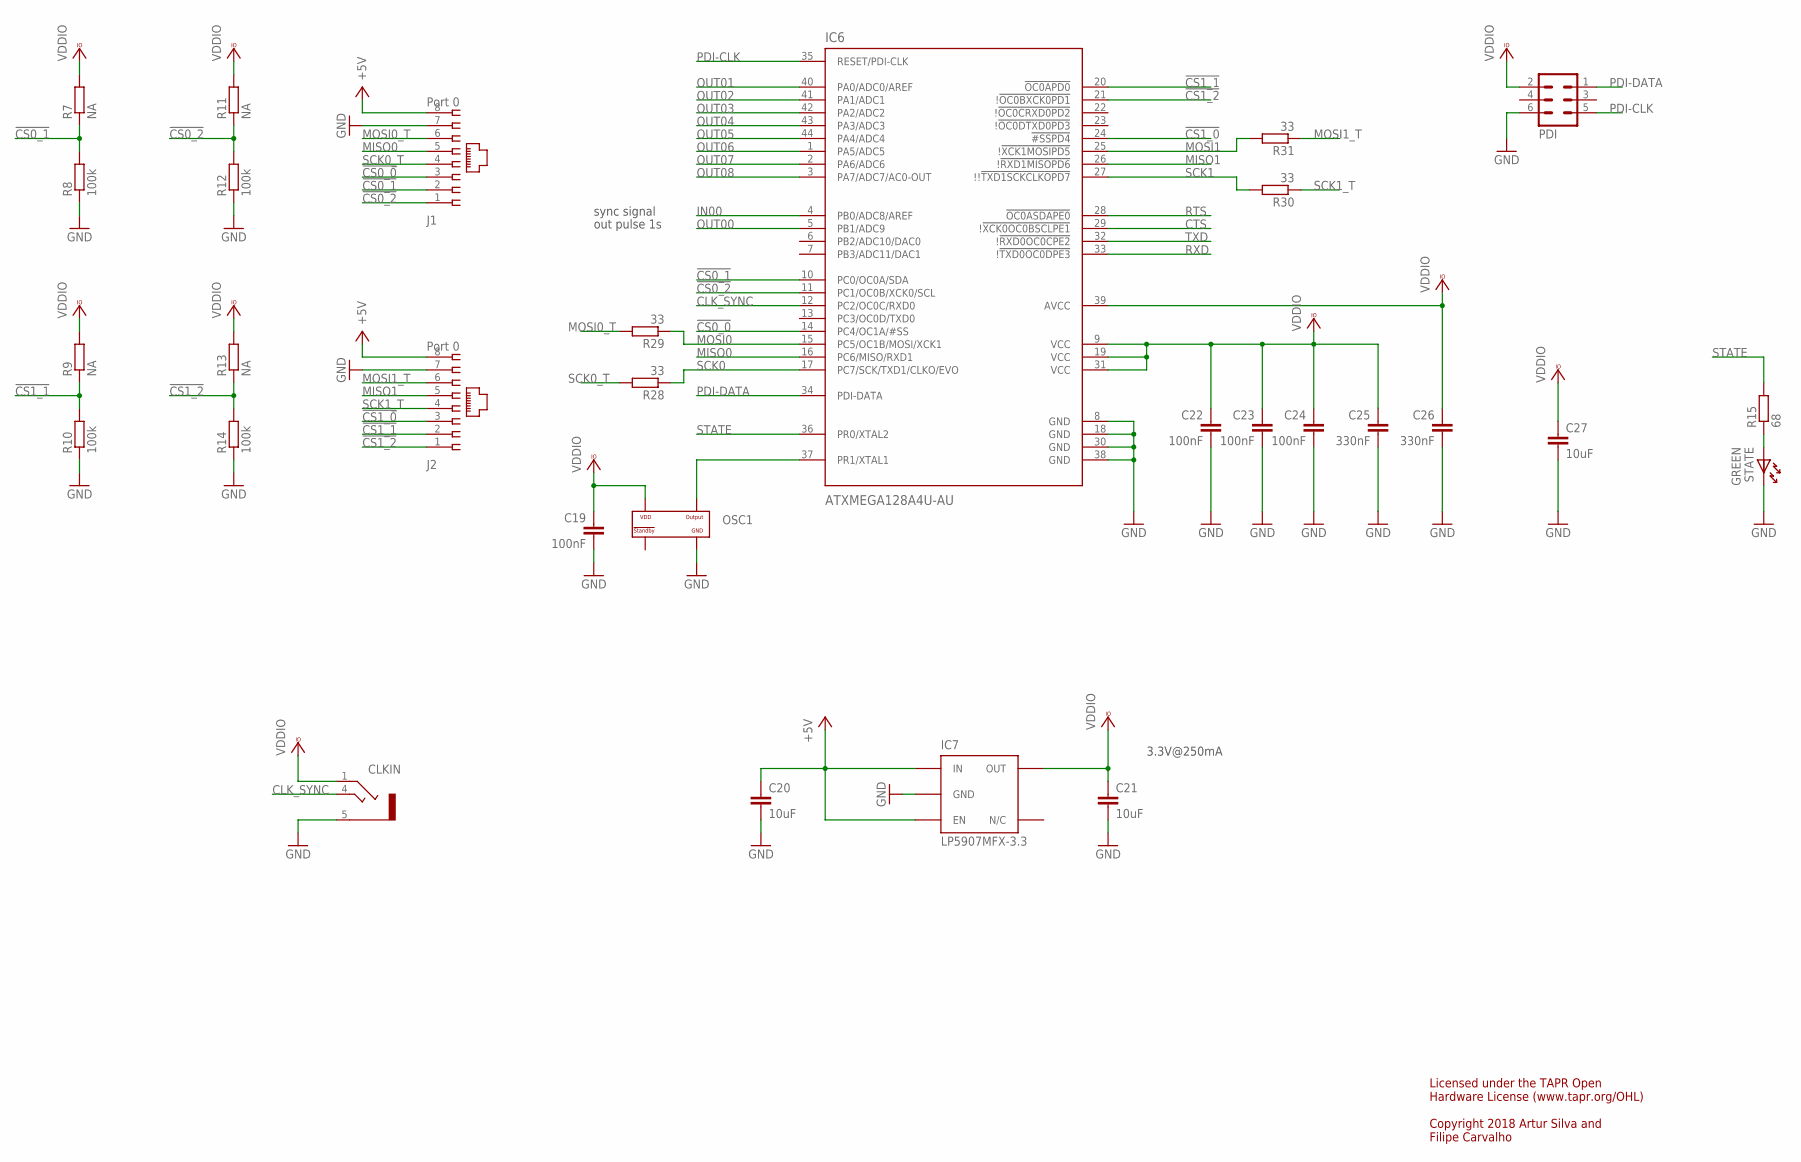
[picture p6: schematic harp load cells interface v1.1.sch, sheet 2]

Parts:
C19, C22, C23, C24: 100nF; C0402
C20, C21, C27: 10uF; C0603
C25, C26: 330nF; C0402
CLKIN: STEREO_JACK; 35RASMT2BHNTRX
IC6: ATXMEGA128A4U-AU; QFP80P1200X1200X120-44N
IC7: LP5907MFX-3.3; TSOT23-5
J1, J2: Port 0; 520426-4
OSC1: OSCILLATOR; OSCILLATOR_3.2X2.5
PDI: MA03-2
R7, R9, R11, R13: NA; R0402
R8, R10, R12, R14: 100k; R0402
R15: 68; R0402
R28, R29, R30, R31: 33; R0402
STATE: GREEN; LED_HAND

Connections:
!CS0_0: IC6.14 (PC4/OC1A/#SS), J1.3
!CS0_1: IC6.10 (PC0/OC0A/SDA), J1.2, R7.1, R8.2
!CS0_2: IC6.11 (PC1/OC0B/XCK0/SCL), J1.1, R11.1, R12.2
!CS1_0: IC6.24 (!#SSPD4), J2.3
!CS1_1: IC6.20 (!OC0APD0), J2.2, R9.1, R10.2
!CS1_2: IC6.21 (!!OC0BXCK0PD1), J2.1, R13.1, R14.2
+5V: C20.1, IC7.1 (IN), IC7.3 (EN), J1.8, J2.8; also elsewhere on the board
CLK_SYNC: CLKIN.4, IC6.12 (PC2/OC0C/RXD0)
CTS: IC6.29 (!!XCK0OC0BSCLPE1); also elsewhere on the board
GND: C19.2, C20.2, C21.2, C22.2, C23.2, C24.2, C25.2, C26.2, C27.2, CLKIN.5, IC6.8 (GND), IC6.18 (GND), IC6.30 (GND), IC6.38 (GND), IC7.2 (GND), J1.7, J2.7, OSC1.P$2 (GND), PDI.6, R8.1, R10.1, R12.1, R14.1, STATE.K; also elsewhere on the board
IN00: IC6.4 (PB0/ADC8/AREF); also elsewhere on the board
MISO0: IC6.16 (PC6/MISO/RXD1), J1.5
MISO1: IC6.26 (!!RXD1MISOPD6), J2.5
MOSI0: IC6.15 (PC5/OC1B/MOSI/XCK1), R29.1
MOSI0_T: J1.6, R29.2
MOSI1: IC6.25 (!!XCK1MOSIPD5), R31.2
MOSI1_T: J2.6, R31.1
unnamed: R15.1, STATE.A
OSC1: IC6.37 (PR1/XTAL1), OSC1.P$3 (OUTPUT)
OUT00: IC6.5 (PB1/ADC9); also elsewhere on the board
OUT01: IC6.40 (PA0/ADC0/AREF); also elsewhere on the board
OUT02: IC6.41 (PA1/ADC1); also elsewhere on the board
OUT03: IC6.42 (PA2/ADC2); also elsewhere on the board
OUT04: IC6.43 (PA3/ADC3); also elsewhere on the board
OUT05: IC6.44 (PA4/ADC4); also elsewhere on the board
OUT06: IC6.1 (PA5/ADC5); also elsewhere on the board
OUT07: IC6.2 (PA6/ADC6); also elsewhere on the board
OUT08: IC6.3 (PA7/ADC7/AC0-OUT); also elsewhere on the board
PDI-CLK: IC6.35 (RESET/PDI-CLK), PDI.5
PDI-DATA: IC6.34 (PDI-DATA), PDI.1
RTS: IC6.28 (!OC0ASDAPE0); also elsewhere on the board
RXD: IC6.33 (!!TXD0OC0DPE3); also elsewhere on the board
SCK0: IC6.17 (PC7/SCK/TXD1/CLKO/EVO), R28.1
SCK0_T: J1.4, R28.2
SCK1: IC6.27 (!!!TXD1SCKCLKOPD7), R30.2
SCK1_T: J2.4, R30.1
STATE: IC6.36 (PR0/XTAL2), R15.2
TXD: IC6.32 (!!RXD0OC0CPE2); also elsewhere on the board
VCCIO: C19.1, C21.1, C22.1, C23.1, C24.1, C25.1, C26.1, C27.1, CLKIN.1, IC6.9 (VCC), IC6.19 (VCC), IC6.31 (VCC), IC6.39 (AVCC), IC7.5 (OUT), OSC1.P$4 (VDD), PDI.2, R7.2, R9.2, R11.2, R13.2; also elsewhere on the board

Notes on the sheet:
3.3V@250mA
Licensed under the TAPR Open Hardware License (www.tapr.org/OHL) Copyright 2018 Artur Silva and Filipe Carvalho
sync signal
out pulse 1s

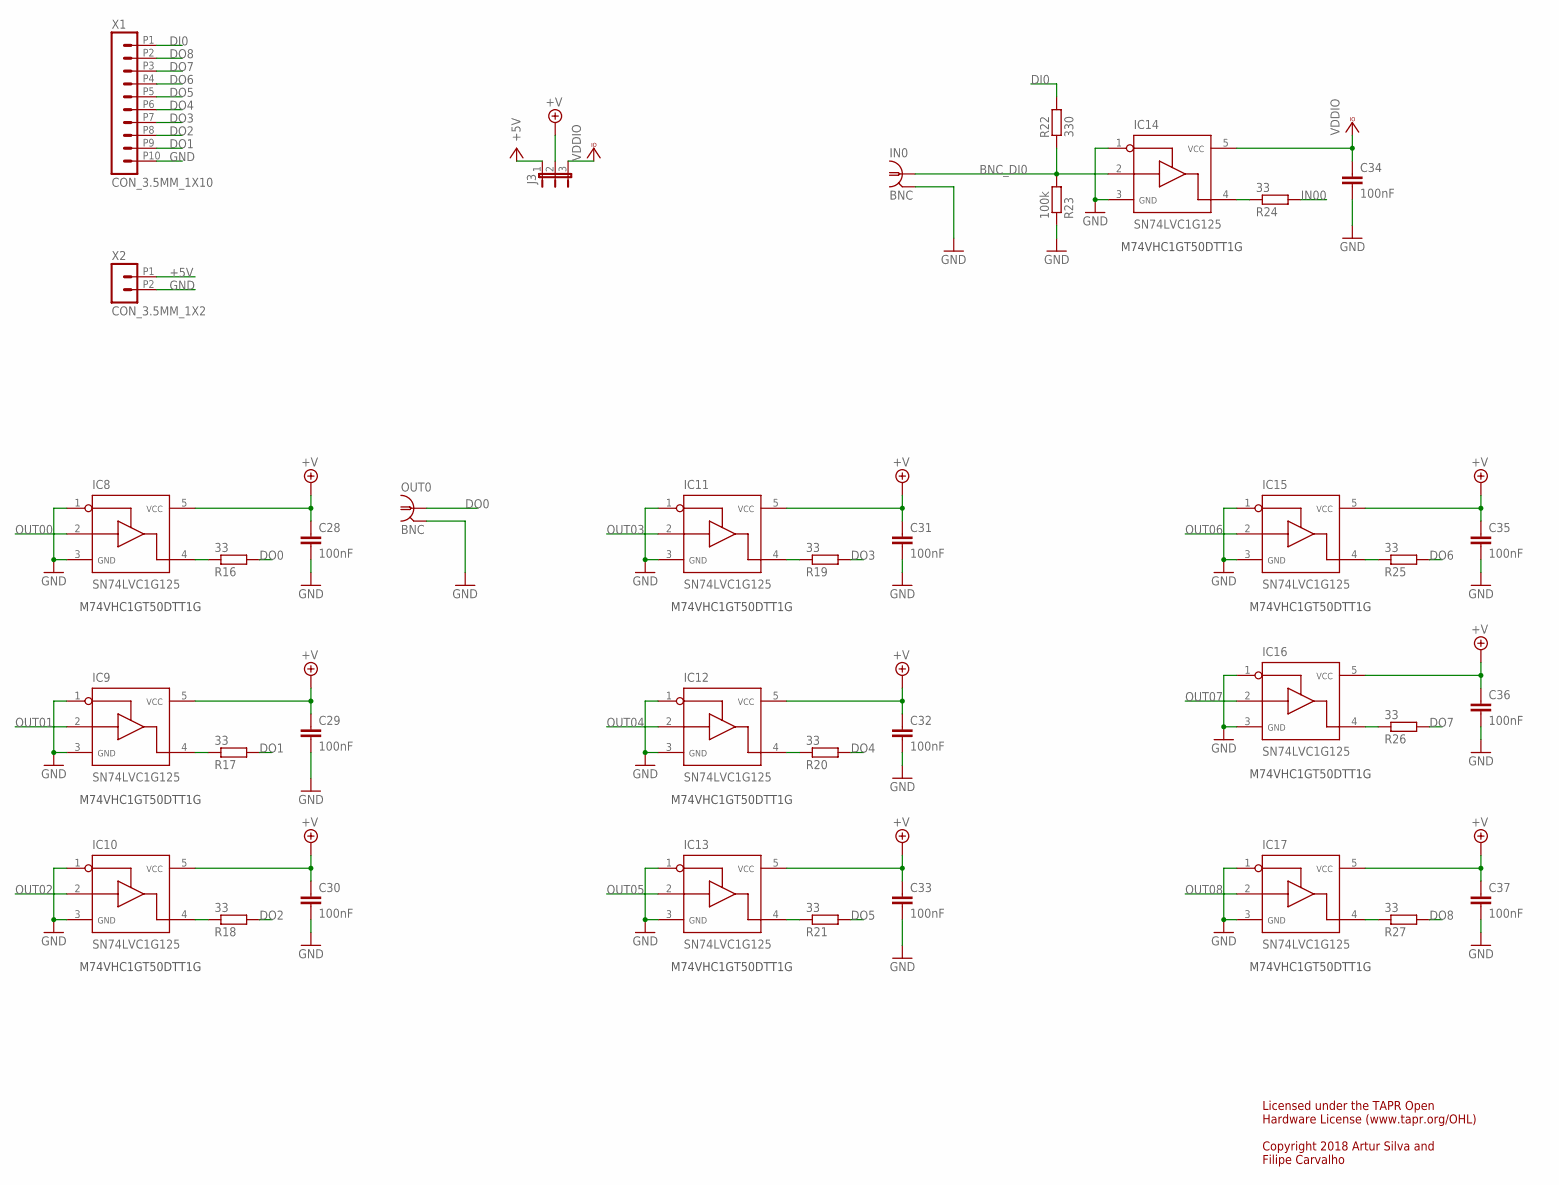
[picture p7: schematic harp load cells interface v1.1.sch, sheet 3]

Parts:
C28, C29, C30, C31, C32, C33, C34, C35, C36, C37: 100nF; C0402
IC8, IC9, IC10, IC11, IC12, IC13, IC14, IC15, IC16, IC17: SN74LVC1G125; SOT23-5
IN0: BNC; BNC_RA
J3: JP2E; JP2
OUT0: BNC; BNC_RA
R16, R17, R18, R19, R20, R21, R24, R25, R26, R27: 33; R0402
R22: 330; R0402
R23: 100k; R0402
X1: CON_3.5MM_1X10
X2: CON_3.5MM_1X2

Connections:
+5V: J3.1, X2.P1 (1); also elsewhere on the board
+V: C28.1, C29.1, C30.1, C31.1, C32.1, C33.1, C35.1, C36.1, C37.1, IC8.5, IC9.5, IC10.5, IC11.5, IC12.5, IC13.5, IC15.5, IC16.5, IC17.5, J3.2
BNC_DI0: IC14.2, IN0.1, R22.2, R23.2
DI0: R22.1, X1.P1 (1)
DO0: OUT0.1, R16.2
DO1: R17.2, X1.P9 (9)
DO2: R18.2, X1.P8 (8)
DO3: R19.2, X1.P7 (7)
DO4: R20.2, X1.P6 (6)
DO5: R21.2, X1.P5 (5)
DO6: R25.2, X1.P4 (4)
DO7: R26.2, X1.P3 (3)
DO8: R27.2, X1.P2 (2)
GND: C28.2, C29.2, C30.2, C31.2, C32.2, C33.2, C34.2, C35.2, C36.2, C37.2, IC8.1, IC8.3, IC9.1, IC9.3, IC10.1, IC10.3, IC11.1, IC11.3, IC12.1, IC12.3, IC13.1, IC13.3, IC14.1, IC14.3, IC15.1, IC15.3, IC16.1, IC16.3, IC17.1, IC17.3, IN0.2, OUT0.2, R23.1, X1.P10 (10), X2.P2 (2); also elsewhere on the board
IN00: R24.2; also elsewhere on the board
unnamed: IC16.4, R26.1
unnamed: IC15.4, R25.1
unnamed: IC10.4, R18.1
unnamed: IC17.4, R27.1
unnamed: IC9.4, R17.1
unnamed: IC12.4, R20.1
unnamed: IC8.4, R16.1
unnamed: IC13.4, R21.1
unnamed: IC11.4, R19.1
unnamed: IC14.4, R24.1
OUT00: IC8.2; also elsewhere on the board
OUT01: IC9.2; also elsewhere on the board
OUT02: IC10.2; also elsewhere on the board
OUT03: IC11.2; also elsewhere on the board
OUT04: IC12.2; also elsewhere on the board
OUT05: IC13.2; also elsewhere on the board
OUT06: IC15.2; also elsewhere on the board
OUT07: IC16.2; also elsewhere on the board
OUT08: IC17.2; also elsewhere on the board
VCCIO: C34.1, IC14.5, J3.3; also elsewhere on the board

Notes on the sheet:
M74VHC1GT50DTT1G
Licensed under the TAPR Open Hardware License (www.tapr.org/OHL) Copyright 2018 Artur Silva and Filipe Carvalho

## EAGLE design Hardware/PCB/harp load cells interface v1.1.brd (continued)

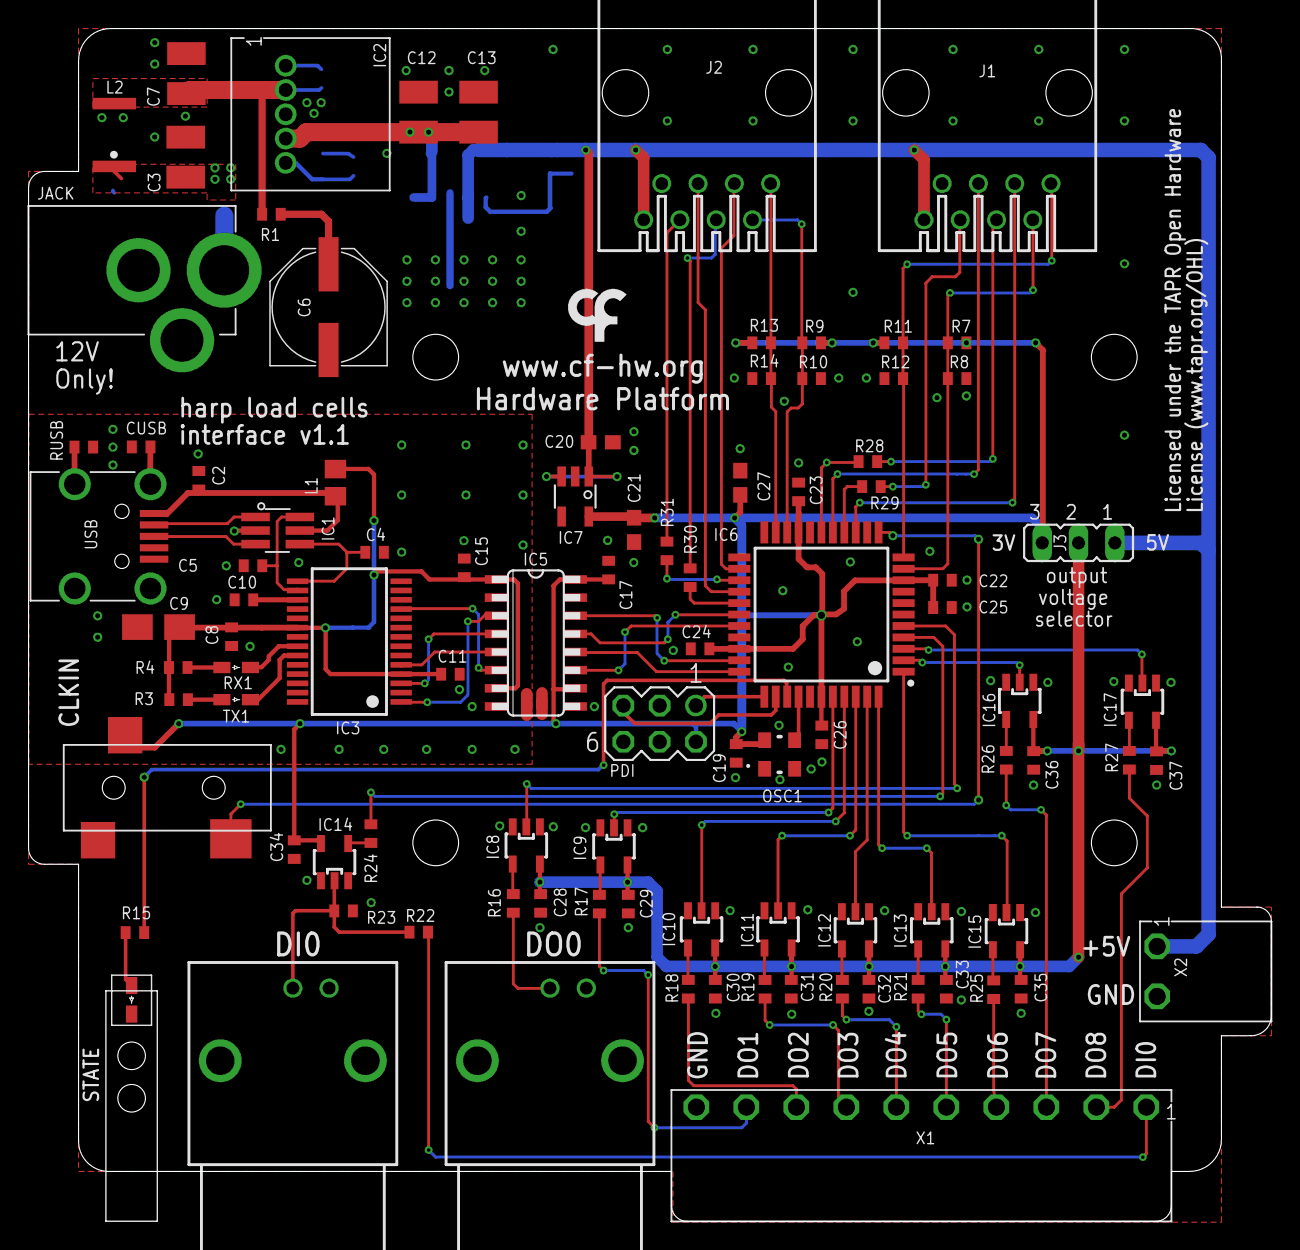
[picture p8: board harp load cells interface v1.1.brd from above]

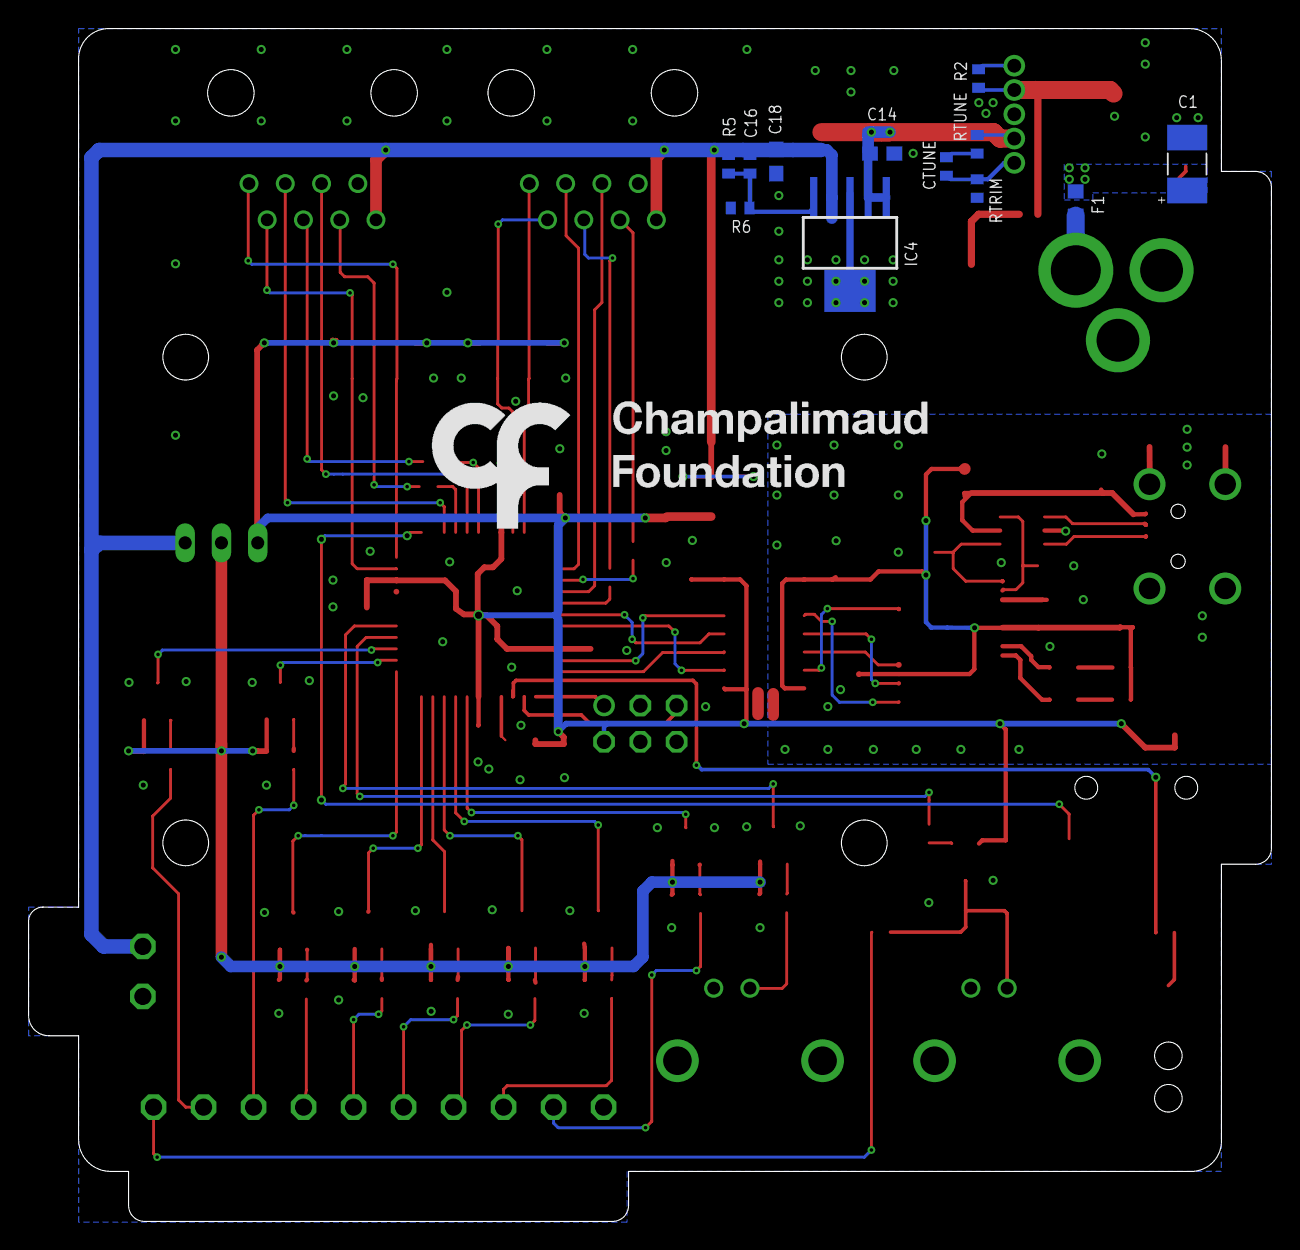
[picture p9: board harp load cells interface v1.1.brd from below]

Board: 2 copper layers, 87.0 x 83.5 mm, 113 parts (13 on the bottom side), 88 nets.

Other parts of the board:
U$1: LED_PIPE_7513D2-L
U$2: LOGO_5
U$4: LOGO_7

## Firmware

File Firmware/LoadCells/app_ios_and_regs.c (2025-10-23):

#include <avr/io.h>
#include "hwbp_core_types.h"
#include "app_ios_and_regs.h"

/************************************************************************/
/* Configure and initialize IOs                                         */
/************************************************************************/
void init_ios(void)
{	/* Configure input pins */
	io_pin2in(&PORTB, 0, PULL_IO_UP, SENSE_IO_EDGES_BOTH);               // DI0
	io_pin2in(&PORTC, 6, PULL_IO_UP, SENSE_IO_EDGES_BOTH);               // MISO0
	io_pin2in(&PORTD, 6, PULL_IO_UP, SENSE_IO_EDGES_BOTH);               // MISO1

	/* Configure input interrupts */
	io_set_int(&PORTB, INT_LEVEL_LOW, 0, (1<<0), false);                 // DI0

	/* Configure output pins */
	io_pin2out(&PORTB, 1, OUT_IO_DIGITAL, IN_EN_IO_EN);                  // DO0
	io_pin2out(&PORTA, 0, OUT_IO_DIGITAL, IN_EN_IO_EN);                  // DO1
	io_pin2out(&PORTA, 1, OUT_IO_DIGITAL, IN_EN_IO_EN);                  // DO2
	io_pin2out(&PORTA, 2, OUT_IO_DIGITAL, IN_EN_IO_EN);                  // DO3
	io_pin2out(&PORTA, 3, OUT_IO_DIGITAL, IN_EN_IO_EN);                  // DO4
	io_pin2out(&PORTA, 4, OUT_IO_DIGITAL, IN_EN_IO_EN);                  // DO5
	io_pin2out(&PORTA, 5, OUT_IO_DIGITAL, IN_EN_IO_EN);                  // DO6
	io_pin2out(&PORTA, 6, OUT_IO_DIGITAL, IN_EN_IO_EN);                  // DO7
	io_pin2out(&PORTA, 7, OUT_IO_DIGITAL, IN_EN_IO_EN);                  // DO8
	io_pin2out(&PORTC, 1, OUT_IO_WIREDAND, IN_EN_IO_EN);                 // CS0_2
	io_pin2out(&PORTC, 0, OUT_IO_WIREDAND, IN_EN_IO_EN);                 // CS0_1
	io_pin2out(&PORTC, 4, OUT_IO_DIGITAL, IN_EN_IO_EN);                  // CS0_0
	io_pin2out(&PORTC, 5, OUT_IO_DIGITAL, IN_EN_IO_DIS);                 // MOSI0
	io_pin2out(&PORTC, 7, OUT_IO_DIGITAL, IN_EN_IO_DIS);                 // SCK0
	io_pin2out(&PORTD, 1, OUT_IO_WIREDAND, IN_EN_IO_EN);                 // CS1_2
	io_pin2out(&PORTD, 0, OUT_IO_WIREDAND, IN_EN_IO_EN);                 // CS1_1
	io_pin2out(&PORTD, 4, OUT_IO_DIGITAL, IN_EN_IO_EN);                  // CS1_0
	io_pin2out(&PORTD, 5, OUT_IO_DIGITAL, IN_EN_IO_DIS);                 // MOSI1
	io_pin2out(&PORTD, 7, OUT_IO_DIGITAL, IN_EN_IO_DIS);                 // SCK1

	/* Initialize output pins */
	clr_DO0;
	clr_DO1;
	clr_DO2;
	clr_DO3;
	clr_DO4;
	clr_DO5;
	clr_DO6;
	clr_DO7;
	clr_DO8;
	set_CS0_2;
	set_CS0_1;
	set_CS0_0;
	clr_MOSI0;
	clr_SCK0;
	set_CS1_2;
	set_CS1_1;
	set_CS1_0;
	clr_MOSI1;
	clr_SCK1;
}

/************************************************************************/
/* Registers' stuff                                                     */
/************************************************************************/
AppRegs app_regs;

uint8_t app_regs_type[] = {
	TYPE_U8,
	TYPE_I16,
	TYPE_U8,
	TYPE_U8,
	TYPE_U8,
	TYPE_U8,
	TYPE_U8,
	TYPE_U8,
	TYPE_U8,
	TYPE_U8,
	TYPE_U16,
	TYPE_U16,
	TYPE_U16,
	TYPE_U16,
	TYPE_U8,
	TYPE_U8,
	TYPE_I16,
	TYPE_I16,
	TYPE_I16,
	TYPE_I16,
	TYPE_I16,
	TYPE_I16,
	TYPE_I16,
	TYPE_I16,
	TYPE_U8,
	TYPE_U8,
	TYPE_U8,
	TYPE_U8,
	TYPE_U8,
	TYPE_U8,
	TYPE_U8,
	TYPE_U8,
	TYPE_U8,
	TYPE_U8,
	TYPE_I16,
	TYPE_I16,
	TYPE_I16,
	TYPE_I16,
	TYPE_I16,
	TYPE_I16,
	TYPE_I16,
	TYPE_I16,
	TYPE_U16,
	TYPE_U16,
	TYPE_U16,
	TYPE_U16,
	TYPE_U16,
	TYPE_U16,
	TYPE_U16,
	TYPE_U16,
	TYPE_U16,
	TYPE_U16,
	TYPE_U16,
	TYPE_U16,
	TYPE_U16,
	TYPE_U16,
	TYPE_U16,
	TYPE_U16,
	TYPE_U8
};

uint16_t app_regs_n_elements[] = {
	1,
	8,
	1,
	1,
	1,
	1,
	1,
	1,
	1,
	1,
	1,
	1,
	1,
	1,
	1,
	1,
	1,
	1,
	1,
	1,
	1,
	1,
	1,
	1,
	1,
	1,
	1,
	1,
	1,
	1,
	1,
	1,
	1,
	1,
	1,
	1,
	1,
	1,
	1,
	1,
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
};

uint8_t *app_regs_pointer[] = {
	(uint8_t*)(&app_regs.REG_START),
	(uint8_t*)(app_regs.REG_LOAD_CELLS),
	(uint8_t*)(&app_regs.REG_DI0),
	(uint8_t*)(&app_regs.REG_DO0),
	(uint8_t*)(&app_regs.REG_THRESHOLDS),
	(uint8_t*)(&app_regs.REG_RESERVED0),
	(uint8_t*)(&app_regs.REG_RESERVED1),
	(uint8_t*)(&app_regs.REG_DI0_CONF),
	(uint8_t*)(&app_regs.REG_DO0_CONF),
	(uint8_t*)(&app_regs.REG_DO0_PULSE),
	(uint8_t*)(&app_regs.REG_DO_SET),
	(uint8_t*)(&app_regs.REG_DO_CLEAR),
	(uint8_t*)(&app_regs.REG_DO_TOGGLE),
	(uint8_t*)(&app_regs.REG_DO_OUT),
	(uint8_t*)(&app_regs.REG_RESERVED2),
	(uint8_t*)(&app_regs.REG_RESERVED3),
	(uint8_t*)(&app_regs.REG_OFFSET_CH0),
	(uint8_t*)(&app_regs.REG_OFFSET_CH1),
	(uint8_t*)(&app_regs.REG_OFFSET_CH2),
	(uint8_t*)(&app_regs.REG_OFFSET_CH3),
	(uint8_t*)(&app_regs.REG_OFFSET_CH4),
	(uint8_t*)(&app_regs.REG_OFFSET_CH5),
	(uint8_t*)(&app_regs.REG_OFFSET_CH6),
	(uint8_t*)(&app_regs.REG_OFFSET_CH7),
	(uint8_t*)(&app_regs.REG_RESERVED4),
	(uint8_t*)(&app_regs.REG_DOS_TH_INV),
	(uint8_t*)(&app_regs.REG_DO0_CH),
	(uint8_t*)(&app_regs.REG_DO1_CH),
	(uint8_t*)(&app_regs.REG_DO2_CH),
	(uint8_t*)(&app_regs.REG_DO3_CH),
	(uint8_t*)(&app_regs.REG_DO4_CH),
	(uint8_t*)(&app_regs.REG_DO5_CH),
	(uint8_t*)(&app_regs.REG_DO6_CH),
	(uint8_t*)(&app_regs.REG_DO7_CH),
	(uint8_t*)(&app_regs.REG_DO0_TH_VALUE),
	(uint8_t*)(&app_regs.REG_DO1_TH_VALUE),
	(uint8_t*)(&app_regs.REG_DO2_TH_VALUE),
	(uint8_t*)(&app_regs.REG_DO3_TH_VALUE),
	(uint8_t*)(&app_regs.REG_DO4_TH_VALUE),
	(uint8_t*)(&app_regs.REG_DO5_TH_VALUE),
	(uint8_t*)(&app_regs.REG_DO6_TH_VALUE),
	(uint8_t*)(&app_regs.REG_DO7_TH_VALUE),
	(uint8_t*)(&app_regs.REG_DO0_TH_UP_MS),
	(uint8_t*)(&app_regs.REG_DO1_TH_UP_MS),
	(uint8_t*)(&app_regs.REG_DO2_TH_UP_MS),
	(uint8_t*)(&app_regs.REG_DO3_TH_UP_MS),
	(uint8_t*)(&app_regs.REG_DO4_TH_UP_MS),
	(uint8_t*)(&app_regs.REG_DO5_TH_UP_MS),
	(uint8_t*)(&app_regs.REG_DO6_TH_UP_MS),
	(uint8_t*)(&app_regs.REG_DO7_TH_UP_MS),
	(uint8_t*)(&app_regs.REG_DO0_TH_DOWN_MS),
	(uint8_t*)(&app_regs.REG_DO1_TH_DOWN_MS),
	(uint8_t*)(&app_regs.REG_DO2_TH_DOWN_MS),
	(uint8_t*)(&app_regs.REG_DO3_TH_DOWN_MS),
	(uint8_t*)(&app_regs.REG_DO4_TH_DOWN_MS),
	(uint8_t*)(&app_regs.REG_DO5_TH_DOWN_MS),
	(uint8_t*)(&app_regs.REG_DO6_TH_DOWN_MS),
	(uint8_t*)(&app_regs.REG_DO7_TH_DOWN_MS),
	(uint8_t*)(&app_regs.REG_EVNT_ENABLE)
};

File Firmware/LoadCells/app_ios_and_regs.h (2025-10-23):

#ifndef _APP_IOS_AND_REGS_H_
#define _APP_IOS_AND_REGS_H_
#include "cpu.h"

void init_ios(void);
/************************************************************************/
/* Definition of input pins                                             */
/************************************************************************/
// DI0                    Description: Input DIO
// MISO0                  Description: MISO0
// MISO1                  Description: MISO1

#define read_DI0 read_io(PORTB, 0)              // DI0
#define read_MISO0 read_io(PORTC, 6)            // MISO0
#define read_MISO1 read_io(PORTD, 6)            // MISO1

/************************************************************************/
/* Definition of output pins                                            */
/************************************************************************/
// DO0                    Description: Output DO0
// DO1                    Description: Output DO1
// DO2                    Description: Output DO2
// DO3                    Description: Output DO3
// DO4                    Description: Output DO4
// DO5                    Description: Output DO5
// DO6                    Description: Output DO6
// DO7                    Description: Output DO7
// DO8                    Description: Output DO8
// CS0_2                  Description: CS0_2 / CS_POT0
// CS0_1                  Description: CS0_1 / CS_ADC0
// CS0_0                  Description: CS0_0 / CONVST0
// MOSI0                  Description: MOSI0
// SCK0                   Description: SCK0
// CS1_2                  Description: CS1_2 / CS_POT1
// CS1_1                  Description: CS1_1 / CS_ADC1
// CS1_0                  Description: CS1_0 / CONVST1
// MOSI1                  Description: MOSI1
// SCK1                   Description: SCK1

/* DO0 */
#define set_DO0 set_io(PORTB, 1)
#define clr_DO0 clear_io(PORTB, 1)
#define tgl_DO0 toggle_io(PORTB, 1)
#define read_DO0 read_io(PORTB, 1)

/* DO1 */
#define set_DO1 set_io(PORTA, 0)
#define clr_DO1 clear_io(PORTA, 0)
#define tgl_DO1 toggle_io(PORTA, 0)
#define read_DO1 read_io(PORTA, 0)

/* DO2 */
#define set_DO2 set_io(PORTA, 1)
#define clr_DO2 clear_io(PORTA, 1)
#define tgl_DO2 toggle_io(PORTA, 1)
#define read_DO2 read_io(PORTA, 1)

/* DO3 */
#define set_DO3 set_io(PORTA, 2)
#define clr_DO3 clear_io(PORTA, 2)
#define tgl_DO3 toggle_io(PORTA, 2)
#define read_DO3 read_io(PORTA, 2)

/* DO4 */
#define set_DO4 set_io(PORTA, 3)
#define clr_DO4 clear_io(PORTA, 3)
#define tgl_DO4 toggle_io(PORTA, 3)
#define read_DO4 read_io(PORTA, 3)

/* DO5 */
#define set_DO5 set_io(PORTA, 4)
#define clr_DO5 clear_io(PORTA, 4)
#define tgl_DO5 toggle_io(PORTA, 4)
#define read_DO5 read_io(PORTA, 4)

/* DO6 */
#define set_DO6 set_io(PORTA, 5)
#define clr_DO6 clear_io(PORTA, 5)
#define tgl_DO6 toggle_io(PORTA, 5)
#define read_DO6 read_io(PORTA, 5)

/* DO7 */
#define set_DO7 set_io(PORTA, 6)
#define clr_DO7 clear_io(PORTA, 6)
#define tgl_DO7 toggle_io(PORTA, 6)
#define read_DO7 read_io(PORTA, 6)

/* DO8 */
#define set_DO8 set_io(PORTA, 7)
#define clr_DO8 clear_io(PORTA, 7)
#define tgl_DO8 toggle_io(PORTA, 7)
#define read_DO8 read_io(PORTA, 7)

/* CS0_2 */
#define set_CS0_2 set_io(PORTC, 1)
#define clr_CS0_2 clear_io(PORTC, 1)
#define tgl_CS0_2 toggle_io(PORTC, 1)
#define read_CS0_2 read_io(PORTC, 1)

/* CS0_1 */
#define set_CS0_1 set_io(PORTC, 0)
#define clr_CS0_1 clear_io(PORTC, 0)
#define tgl_CS0_1 toggle_io(PORTC, 0)
#define read_CS0_1 read_io(PORTC, 0)

/* CS0_0 */
#define set_CS0_0 set_io(PORTC, 4)
#define clr_CS0_0 clear_io(PORTC, 4)
#define tgl_CS0_0 toggle_io(PORTC, 4)
#define read_CS0_0 read_io(PORTC, 4)

/* MOSI0 */
#define set_MOSI0 set_io(PORTC, 5)
#define clr_MOSI0 clear_io(PORTC, 5)
#define tgl_MOSI0 toggle_io(PORTC, 5)
#define read_MOSI0 read_io(PORTC, 5)

/* SCK0 */
#define set_SCK0 set_io(PORTC, 7)
#define clr_SCK0 clear_io(PORTC, 7)
#define tgl_SCK0 toggle_io(PORTC, 7)
#define read_SCK0 read_io(PORTC, 7)

/* CS1_2 */
#define set_CS1_2 set_io(PORTD, 1)
#define clr_CS1_2 clear_io(PORTD, 1)
#define tgl_CS1_2 toggle_io(PORTD, 1)
#define read_CS1_2 read_io(PORTD, 1)

/* CS1_1 */
#define set_CS1_1 set_io(PORTD, 0)
#define clr_CS1_1 clear_io(PORTD, 0)
#define tgl_CS1_1 toggle_io(PORTD, 0)
#define read_CS1_1 read_io(PORTD, 0)

/* CS1_0 */
#define set_CS1_0 set_io(PORTD, 4)
#define clr_CS1_0 clear_io(PORTD, 4)
#define tgl_CS1_0 toggle_io(PORTD, 4)
#define read_CS1_0 read_io(PORTD, 4)

/* MOSI1 */
#define set_MOSI1 set_io(PORTD, 5)
#define clr_MOSI1 clear_io(PORTD, 5)
#define tgl_MOSI1 toggle_io(PORTD, 5)
#define read_MOSI1 read_io(PORTD, 5)

/* SCK1 */
#define set_SCK1 set_io(PORTD, 7)
#define clr_SCK1 clear_io(PORTD, 7)
#define tgl_SCK1 toggle_io(PORTD, 7)
#define read_SCK1 read_io(PORTD, 7)


/************************************************************************/
/* Registers' structure                                                 */
/************************************************************************/
typedef struct
{
	uint8_t REG_START;
	int16_t REG_LOAD_CELLS[8];
	uint8_t REG_DI0;
	uint8_t REG_DO0;
	uint8_t REG_THRESHOLDS;
	uint8_t REG_RESERVED0;
	uint8_t REG_RESERVED1;
	uint8_t REG_DI0_CONF;
	uint8_t REG_DO0_CONF;
	uint8_t REG_DO0_PULSE;
	uint16_t REG_DO_SET;
	uint16_t REG_DO_CLEAR;
	uint16_t REG_DO_TOGGLE;
	uint16_t REG_DO_OUT;
	uint8_t REG_RESERVED2;
	uint8_t REG_RESERVED3;
	int16_t REG_OFFSET_CH0;
	int16_t REG_OFFSET_CH1;
	int16_t REG_OFFSET_CH2;
	int16_t REG_OFFSET_CH3;
	int16_t REG_OFFSET_CH4;
	int16_t REG_OFFSET_CH5;
	int16_t REG_OFFSET_CH6;
	int16_t REG_OFFSET_CH7;
	uint8_t REG_RESERVED4;
	uint8_t REG_DOS_TH_INV;
	uint8_t REG_DO0_CH;
	uint8_t REG_DO1_CH;
	uint8_t REG_DO2_CH;
	uint8_t REG_DO3_CH;
	uint8_t REG_DO4_CH;
	uint8_t REG_DO5_CH;
	uint8_t REG_DO6_CH;
	uint8_t REG_DO7_CH;
	int16_t REG_DO0_TH_VALUE;
	int16_t REG_DO1_TH_VALUE;
	int16_t REG_DO2_TH_VALUE;
	int16_t REG_DO3_TH_VALUE;
	int16_t REG_DO4_TH_VALUE;
	int16_t REG_DO5_TH_VALUE;
	int16_t REG_DO6_TH_VALUE;
	int16_t REG_DO7_TH_VALUE;
	uint16_t REG_DO0_TH_UP_MS;
	uint16_t REG_DO1_TH_UP_MS;
	uint16_t REG_DO2_TH_UP_MS;
	uint16_t REG_DO3_TH_UP_MS;
	uint16_t REG_DO4_TH_UP_MS;
	uint16_t REG_DO5_TH_UP_MS;
	uint16_t REG_DO6_TH_UP_MS;
	uint16_t REG_DO7_TH_UP_MS;
	uint16_t REG_DO0_TH_DOWN_MS;
	uint16_t REG_DO1_TH_DOWN_MS;
	uint16_t REG_DO2_TH_DOWN_MS;
	uint16_t REG_DO3_TH_DOWN_MS;
	uint16_t REG_DO4_TH_DOWN_MS;
	uint16_t REG_DO5_TH_DOWN_MS;
	uint16_t REG_DO6_TH_DOWN_MS;
	uint16_t REG_DO7_TH_DOWN_MS;
	uint8_t REG_EVNT_ENABLE;
} AppRegs;
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

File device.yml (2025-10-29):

%YAML 1.1
---
# yaml-language-server: $schema=https://harp-tech.org/draft-02/schema/device.json
device: LoadCells
whoAmI: 1232
firmwareVersion: "1.2"
hardwareTargets: "1.0"
registers:
  AcquisitionState:
    address: 32
    access: Write
    type: U8
    maskType: EnableFlag
    description: Enables the data acquisition.
  LoadCellData:
    address: 33
    type: S16
    length: 8
    access: Event
    description: Value of single ADC read from all load cell channels.
    payloadSpec:
      Channel0:
        offset: 0
      Channel1:
        offset: 1
      Channel2:
        offset: 2
      Channel3:
        offset: 3
      Channel4:
        offset: 4
      Channel5:
        offset: 5
      Channel6:
        offset: 6
      Channel7:
        offset: 7
  DigitalInputState:
    address: 34
    access: Event
    type: U8
    maskType: DigitalInputs
    description: Status of the digital input pin 0. An event will be emitted when DI0Trigger == None.
  SyncOutputState:
    address: 35
    access: Event
    type: U8
    maskType: SyncOutputs
    description: Status of the digital output pin 0. An periodic event will be emitted when DO0Sync == ToggleEachSecond.
  BufferThresholdState:
    address: 36
    access: Read
    visibility: private
    type: U8
    description: State of the buffer thresholds.
  Reserved0: &ReservedReg
    address: 37
    access: Read
    visibility: private
    type: U8
    description: Reserved
  Reserved1:
    <<: *ReservedReg
    address: 38
  DI0Trigger:
    address: 39
    access: Write
    type: U8
    maskType: TriggerConfig
    description: Configuration of the digital input pin 0.
  DO0Sync:
    address: 40
    access: Write
    type: U8
    maskType: SyncConfig
    description: Configuration of the digital output pin 0.
  DO0PulseWidth:
    address: 41
    access: Write
    type: U8
    minValue: 1
    maxValue: 255
    description: Pulse duration (ms) for the digital output pin 0. The pulse will only be emitted when DO0Sync == Pulse.
  DigitalOutputSet: &output
    address: 42
    type: U16
    access: Write
    maskType: DigitalOutputs
    description: Set the specified digital output lines.
  DigitalOutputClear:
    <<: *output
    address: 43
    description: Clear the specified digital output lines.
  DigitalOutputToggle:
    <<: *output
    address: 44
    description: Toggle the specified digital output lines
  DigitalOutputState:
    <<: *output
    address: 45
    access: [Write, Event]
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

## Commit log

2018-04-13 Added antire set of files (still lacing threshold routines).
    [registers.xls]
2018-04-16 Corrected group mask of registers DOx_CH.
    [registers.xls]
2018-04-16 Changed the code in order to update the slave boards' potentiometers even if not acquiring data.
2018-04-17 Corrected issue that was writing load cells readings to zero when using long cables.
2018-04-17 Added a waiting time of 250 ms before update the potentiometers when a board is connected.
2018-04-27 Added filter to the digital input DI0.
2022-12-17 Add PCB files
    [harp load cells interface v1.1.brd, harp load cells interface v1.1.sch, harp load cells v1.1.brd, harp load cells v1.1.sch]
2022-12-17 Add PCB BOMs
    [harp load cells interface v1.1_BOM.xlsx, harp load cells v1.1_BOM.xlsx]
2022-12-23 refactor repository structure
    [harp load cells interface v1.1.brd, harp load cells interface v1.1.sch, harp load cells interface v1.1_BOM.xlsx, harp load cells v1.1.brd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]
2023-04-17 Add first version of the device schema
2023-04-17 Add generated Device classes
2023-04-19 Update device schema to reflect the PCB DO numbering
2023-04-19 Update interface to reflect last device schema spec
2023-06-02 Update schema for consistency with Device.AnalogInput
2023-06-02 Update `Device` classes to new schema
2023-06-07 Improve device schema
2023-06-07 Update `Device` classes
2023-08-11 Updated hardware version to the latest PCB version.
2023-08-19 Update pcb.png asset
2023-09-14 Update device.yml firmware version
2024-11-09 Embed device.yml and bump release
2024-11-10 Favor harp-tech as source of device schema

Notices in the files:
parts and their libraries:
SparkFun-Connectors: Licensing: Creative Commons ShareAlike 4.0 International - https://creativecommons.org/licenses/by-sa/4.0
